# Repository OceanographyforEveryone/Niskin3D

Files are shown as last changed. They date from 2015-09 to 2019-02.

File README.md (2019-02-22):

Niskin3D
========

### Background

Niskin3D is low-cost, open-source water sampler made from 3D-printed parts and controlled by a waterproof servo. 

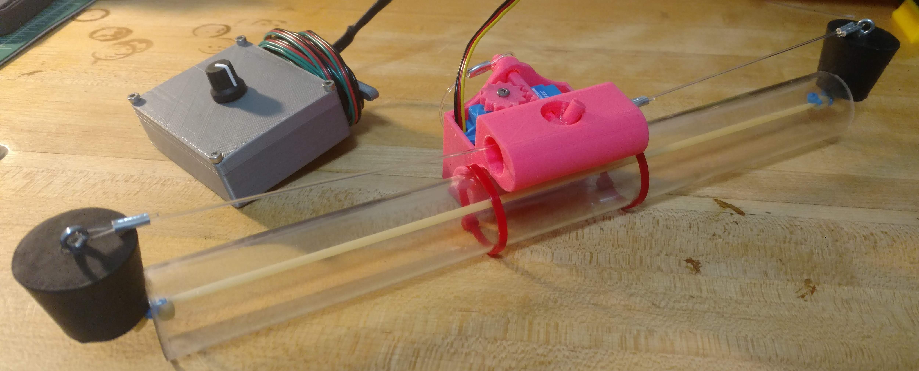
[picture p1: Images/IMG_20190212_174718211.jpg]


### Overview

The Niskin bottle, a seemingly simple tube designed to take water samples at discrete depths, is one of the most important tools of oceanography. Coupled with a CTD, an array of Niskin bottles fit into a rosette provides everything an oceanographer needs to profile the ocean. Niskin bottles are neither cheap nor particularly easy to use. A commercial rosette requires a winch to launch and recover, requiring both a vessel and a crew to deploy. For informal, unaffiliated, or unfunded researchers, as well as citizen scientists or any researcher working on a tight budget, getting high-quality, discrete water samples is an ongoing challenge. 

The Niskin3D lowers the cost of discrete-depth water sampling and makes this common tool of oceanographic research available to anyone. 

### Current Status

Undergoing major redesign as of 2/12/2019.

### Bill of Materials

We use Amazon Affiliate links because the small kickback helps fund more projects like this, but almost everything can be sourced through hobby shops, hardware stores, and other retailers. These recommendations don't necessarily represent the cheapest prices but rather the actual components we bought for this project or the closest approximation we could find. Some components are batched and may be available elsewhere in smaller quantities. Other high-test line and elastics can be used in place of the monofilament and sligshot tubing. 

**Niskin3D Bottle and Trigger Mechanism**

Part | Supplier | Price | Link
--- | --- | --- | ---
HiTec 32646W HS-646WP Water Proof Analog Servo (IP-67 Rated) | Amazon | $44.36 | https://amzn.to/2E60NLb
Clear Polycarbonate Tubing, 1-1/8" ID, 1-1/4" OD, 1/16" Wall, 4' Length | Amazon | $11.72| https://amzn.to/2E66wRa
Solid Rubber Stoppers - Size 6 | Amazon or local hardware store | $10.88 | https://amzn.to/2E6pEyw
Eye Screw with 12mm hoop | Amazon or local hardware store | $6.89 | https://amzn.to/2U5frI4
150-lb Monofilament with 1.3mm Crimps | Amazon or local fishing store | $12.99 | https://amzn.to/2tmStAh
3x5mm Natural Latex Rubber Band Tube Tubing for Slingshots | Amazon or local sportiing good store | $7.55 | https://amzn.to/2GGn57R
8" Cable Ties | Amazon or local hardware store | $6.99 | https://amzn.to/2E7rf76

**Niskin3D Control Box**

Part | Supplier | Price | Link
--- | --- | --- | ---
Arduino Leonardo | Amazon or Arduino.org | $22.19 | https://amzn.to/2E66RDo
2K Ohm Potentiometer | Amazon | $13.21 | https://amzn.to/2SGJUil
Ribbon Cable | Amazon | $6.98 | https://amzn.to/2UPQDDK
M3 Hex Socket Screws | Amazon | $10.99 | https://amzn.to/2GnfeN8

Consumables include heat shrink tubing, solder, and hook-up wire. Tools include a crimper, flush cut pliers, hex wrench, and a soldering station. We recommend using PLA filament for the 3D-printable parts. 

### Build Instructions

**3D Printing.** Print all parts in [3D_Printer_Files](https://github.com/OceanographyforEveryone/Niskin3D/tree/master/3D_Printer_Files) (ignore the folder labelled old unless you want to build the original Niskin3D) using your prefered PLA filament. NiskinRecieverLinear.stl, PowerBox.stl, and PowerBoxBottom.stl should be printed at 200 micron resolution with 20% infill. All other components should be printed at 100 micro resolution with 100% infill. 

**Servo Assembly.** Remove the included servo horn and slot the servo wheel onto the exposed metal gear. Use the included screw to secure the wheel. 

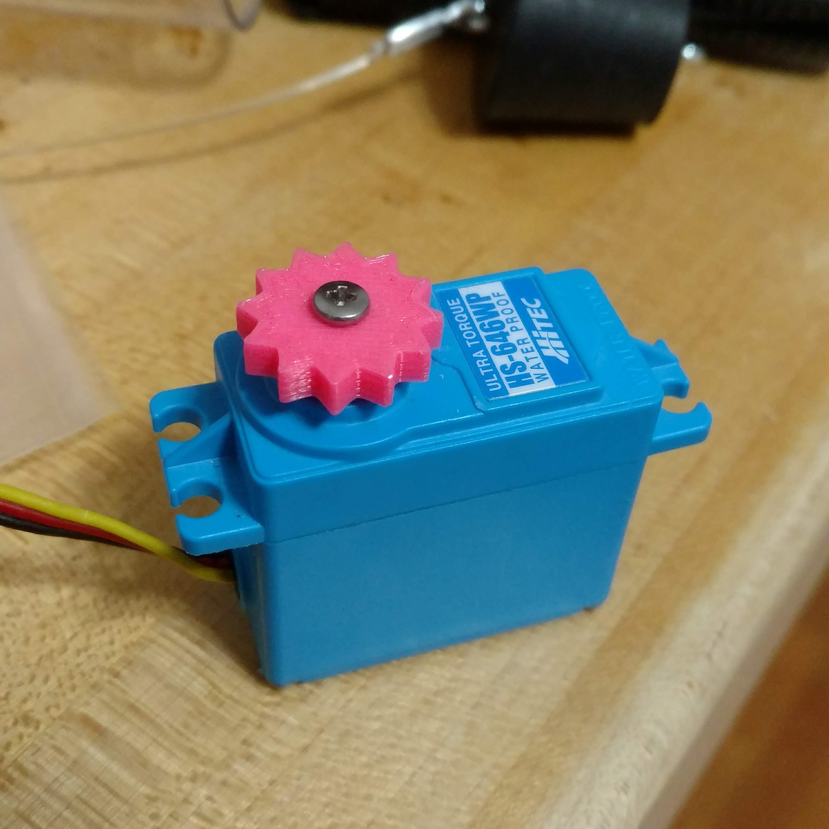
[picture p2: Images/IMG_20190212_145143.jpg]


**Receiver Assembly.** Insert the servo into the reciever such that when holding the reciever with the trigger tube facing away from you, the servo wheel sits to the right of the trigger slot. 

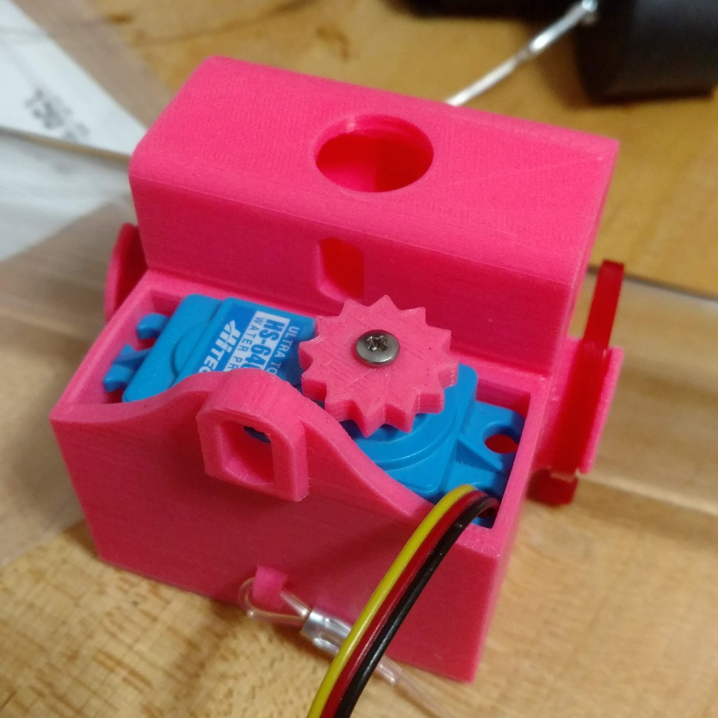
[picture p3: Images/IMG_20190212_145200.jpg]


Rotate the servo wheel counter-clockwise until it reaches its limit. Slot the trigger through the external trigger hole and across the servo wheel and just barely into the main trigger slot. The innermost tooth of the trigger should fully catch against the servo wheel. Secure the trigger to the reciever by looping monofilament through the hole in the trigger and the loop near the base of the reciever to prevent the trigger from being lost if it comes loose.

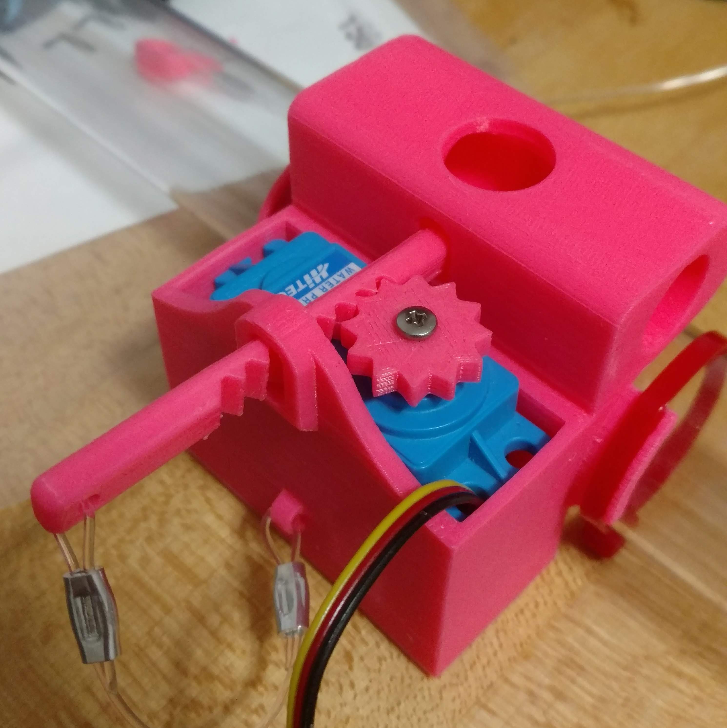
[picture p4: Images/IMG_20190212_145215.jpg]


**Bottle Assembly.** Cut the polcarbonate tube to the deisred length. Screw the eye screws into the center of both faces of the rubber stopper. Crimp monofilament onto the wider face of each stopper. On one stopper, measure out enough line to reach the hole in the center of the reciever trigger tube and crimp a large loop into the monofilament. On the other stopper, measure out enough line to  reach the hole in the center of the reciever trigger tube with enough length the the pin can sit in the center of the trigger tube and crimp the monofilament around the pin with enough slack that the line can sit in the notch on the pin. 

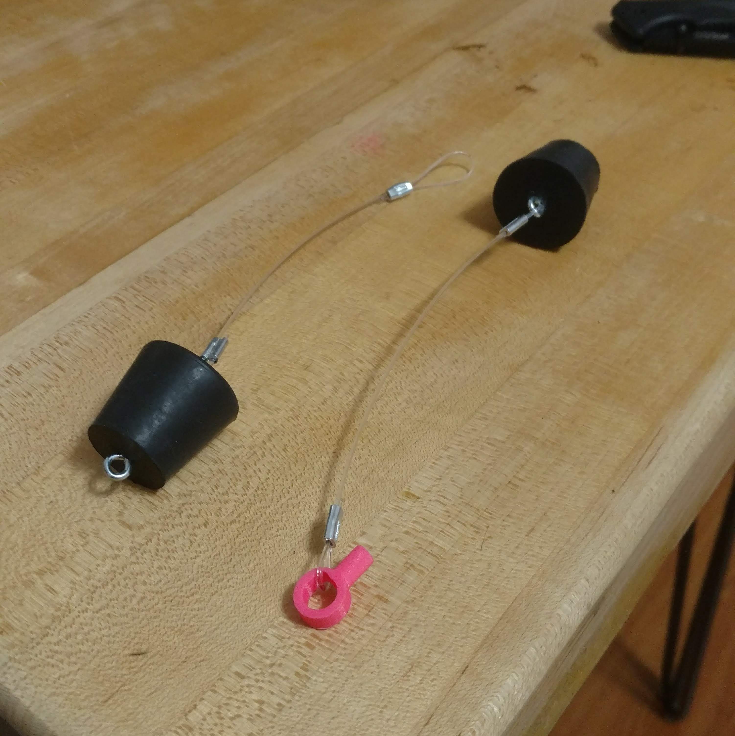
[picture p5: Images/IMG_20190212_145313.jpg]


Measure out enough latex tubing that it can hold the two rubber stoppers tightly in the polycarbonate tube. On the inner face of one rubber stopper, ziptie the latex tubing to the eye bolt. Feed the latex tubing through the polycarbonate tube, pull it tight, and ziptie it to the inner eye bolt on the other rubber stopper. 

**Power Box Assembly.** _Only do this if you need an independently-triggered Niskin bottle. Otherwise, connect the servo to the hardware of your choice using a standard servo interface._  Flash [NiskinServo.ino](https://github.com/OceanographyforEveryone/Niskin3D/tree/master/NiskinServo) to the Arduino. Solder header wires to the potentiometer. Screw the potentiometer into the large hole in the center of the Power Box Bottom. Connect the outer leads of the potentiometer to ground and Vin. Connect the center lead to Analog Pin 0. Measure out as much ribbon cable as you need for the servo. Feed ribbon cable through hole next to the spool on the case. Connect servo to ground and 5V. Connect signal line to Digital Pin 7. Close case and secure with M3 screws.

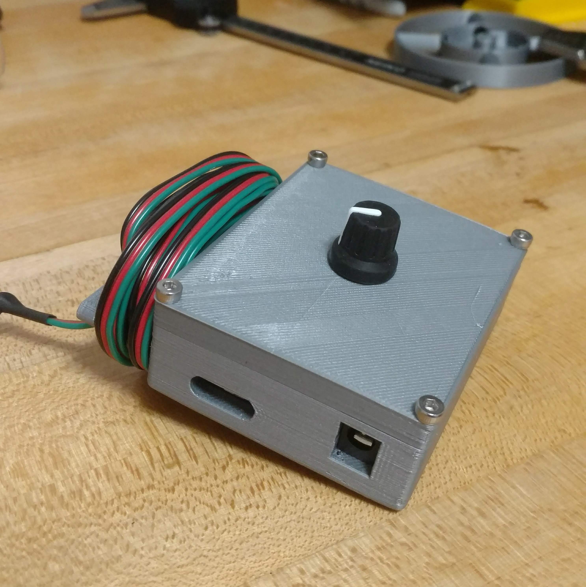
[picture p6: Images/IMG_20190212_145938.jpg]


### Priming the trigger

Pull the rubber stoppers out of the polycarbonate tube. Slot the pin into the trigger tube such that the point sticks up through the central hole. Rotate the servo clockwise to drive the trigger through the pin and into the wall of the trigger tube. Slot the loop on the other stopper through the trigger tube and over the pin such that it catches and rotates the pin towards the opposite rubber stopper. 

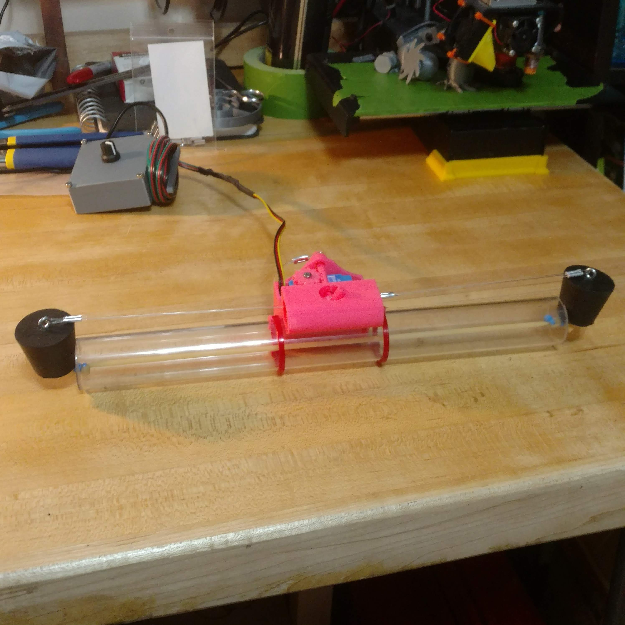
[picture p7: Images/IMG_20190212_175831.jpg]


Ensure that the rubber stoppers are situated so that once the pin is released both stoppers will be pulled into the polycarbonate tube and seal it. 

Your Niskin bottle is now primed. 

### Triggering

Activate the servo and rotate it counter-clockwise to pull the trigger and release the pin. 

### Resources and Media

[Oceanography for Everyone](http://oceanographyforeveryone.com/)

[Niskin3D: the open-source water sampler](https://www.thingiverse.com/thing:3421202)

[A 3D-printable, drone and ROV-mountable, water sampler](http://www.southernfriedscience.com/?p=18730)

[The next generation open-source, 3D-printable Niskin bottle has arrived!](http://www.southernfriedscience.com/the-next-generation-open-source-3d-printable-niskin-bottle-has-arrived/)

### Acknowledgments 

Design and testing of the Niskin3D conducted by Andrew Thaler.

### Code of Conduct

Please review our [Contributor Code of Conduct](https://github.com/OceanographyforEveryone/Niskin3D/blob/master/CODE_OF_CONDUCT.md) prior to your first contribution.

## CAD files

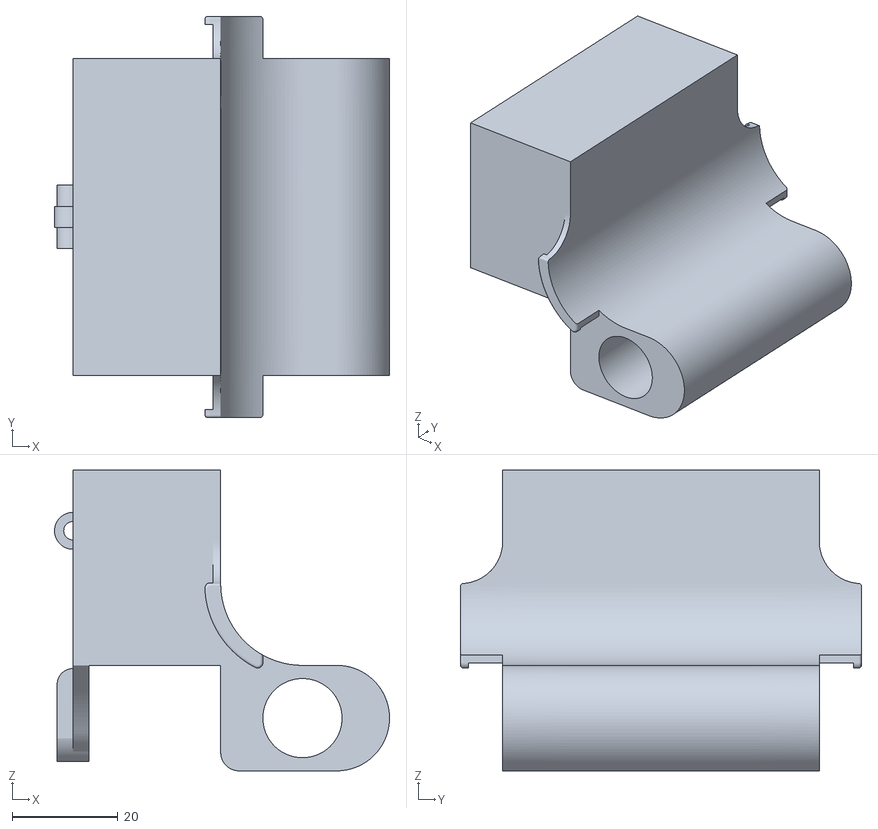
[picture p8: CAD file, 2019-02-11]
3D_Printer_Files/NiskinRecieverLinear.stl
63.5 x 76.0 x 57.0

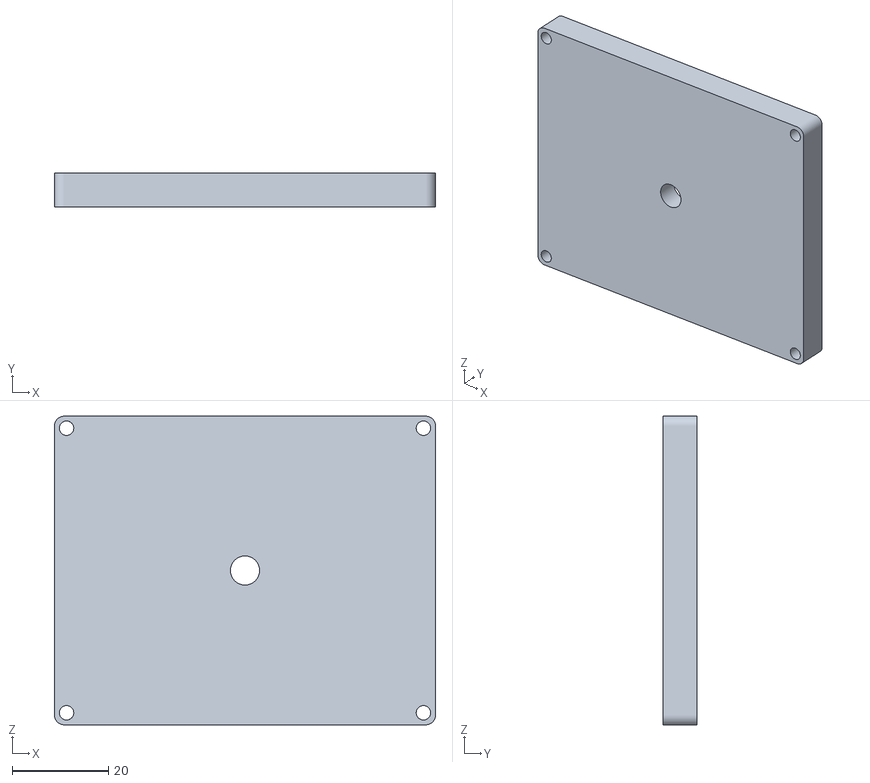
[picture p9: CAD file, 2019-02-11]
3D_Printer_Files/PowerBoxBottom.stl
79.0 x 7.00 x 64.0

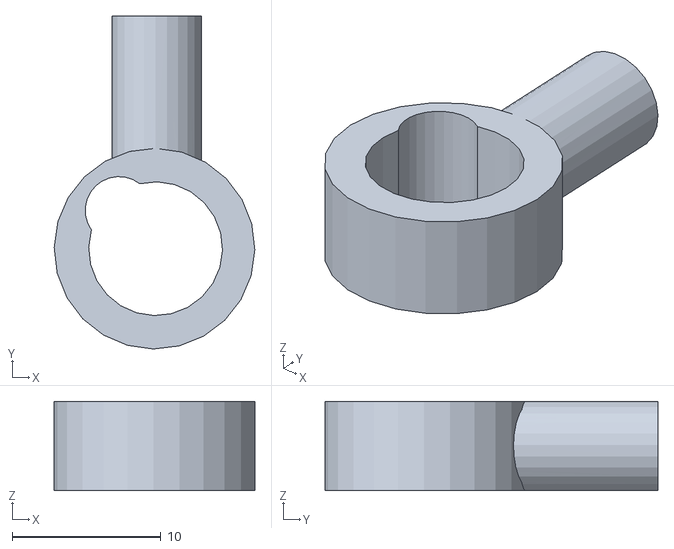
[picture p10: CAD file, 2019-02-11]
3D_Printer_Files/Niskin3DPin.stl
13.5 x 22.4 x 6.00

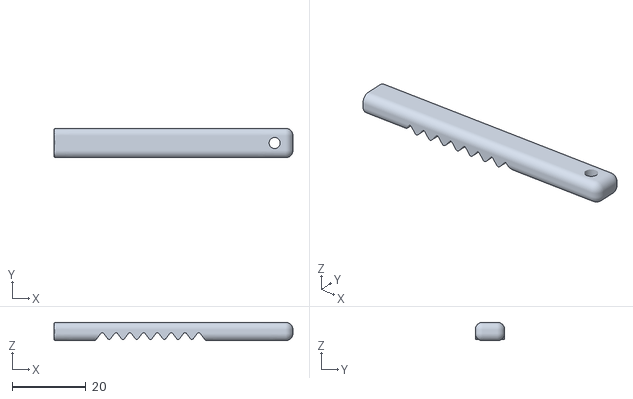
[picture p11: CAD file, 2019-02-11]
3D_Printer_Files/NiskinTriggerLinear.stl
65.0 x 8.00 x 5.00

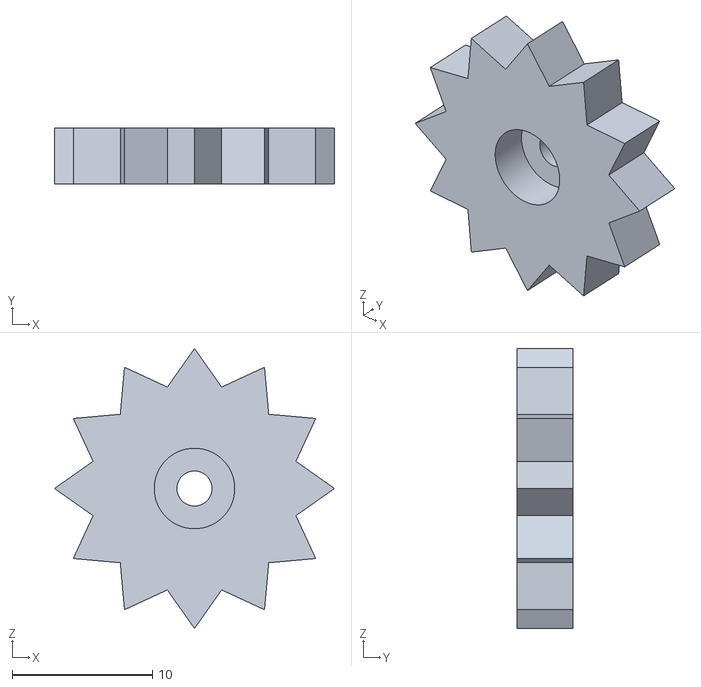
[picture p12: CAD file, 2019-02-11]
3D_Printer_Files/ServoWheel.stl
20.0 x 4.00 x 20.0

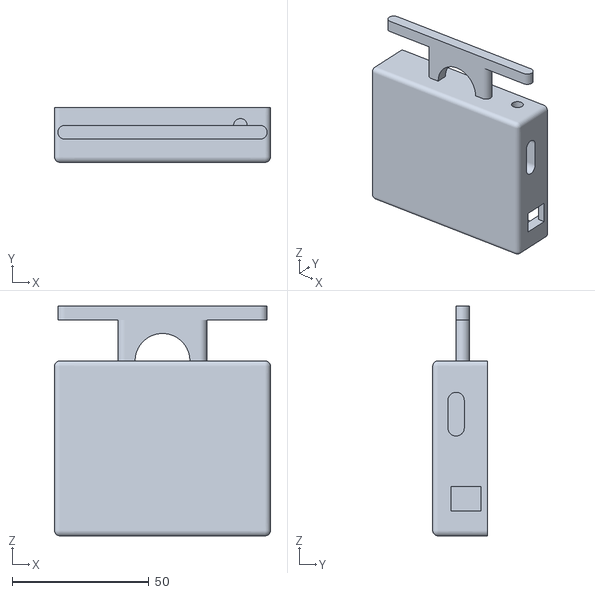
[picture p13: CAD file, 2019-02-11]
3D_Printer_Files/PowerBox.stl
79.0 x 20.0 x 84.0

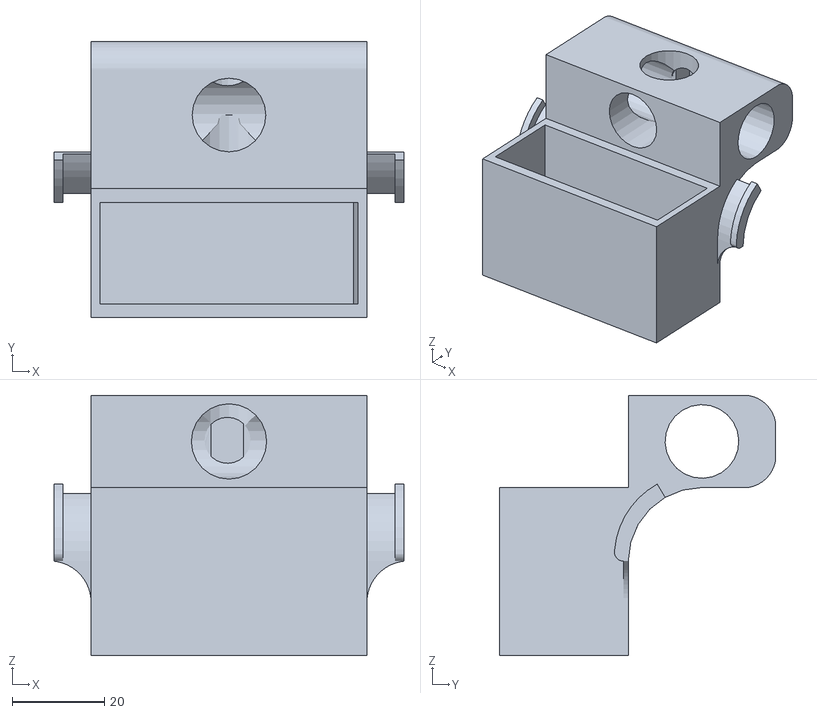
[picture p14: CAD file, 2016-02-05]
3D_Printer_Files/NiskinRecieverHS646WP.stl
76.0 x 60.0 x 56.5

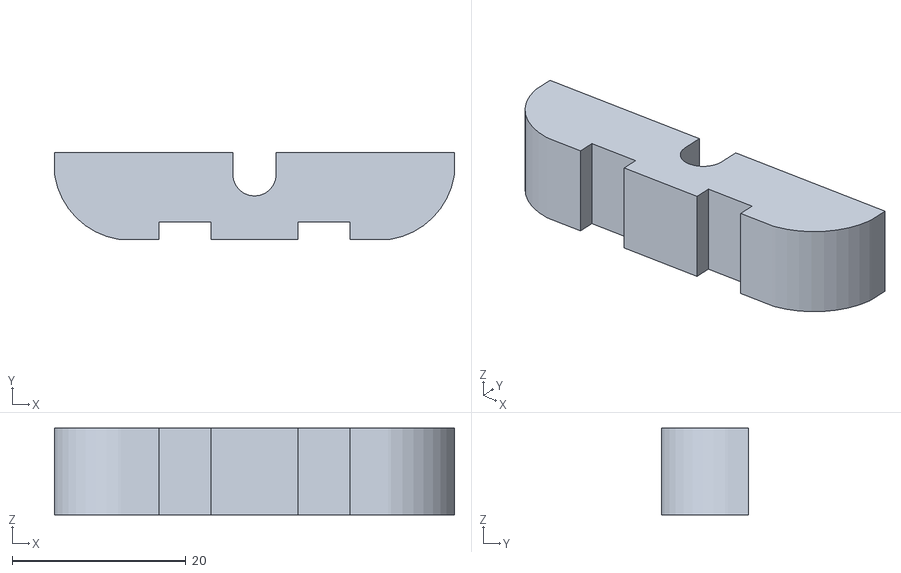
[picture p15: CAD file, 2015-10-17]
3D_Printer_Files/OpenROVNiskinRear.stl
46.0 x 10.0 x 10.00

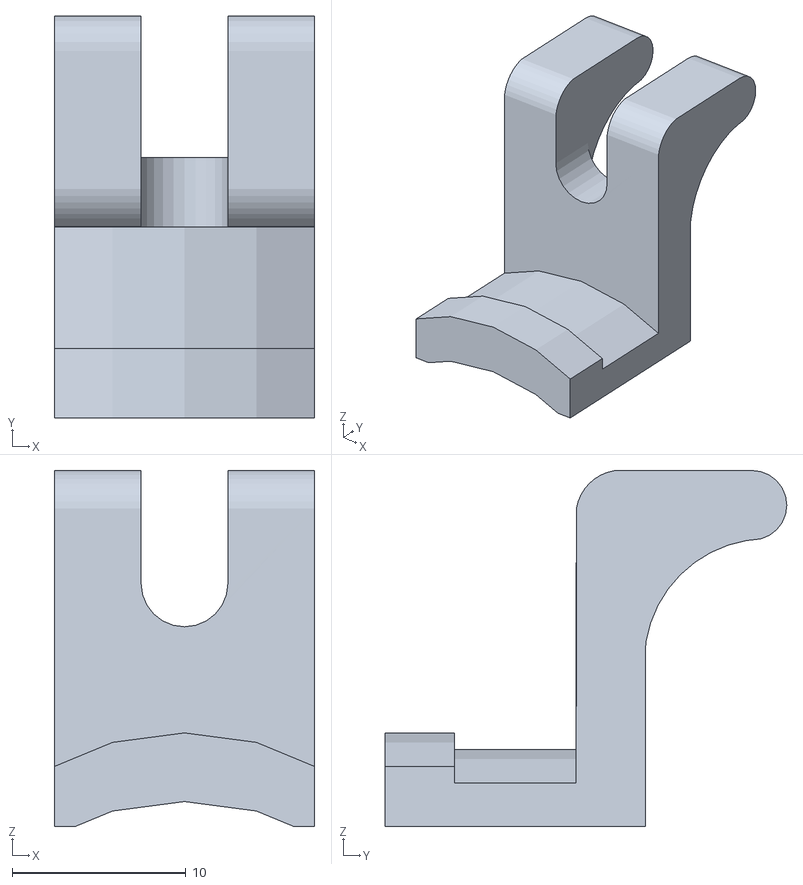
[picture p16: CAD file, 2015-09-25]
3D_Printer_Files/NiskinEndCatch.stl
15.0 x 23.1 x 20.5

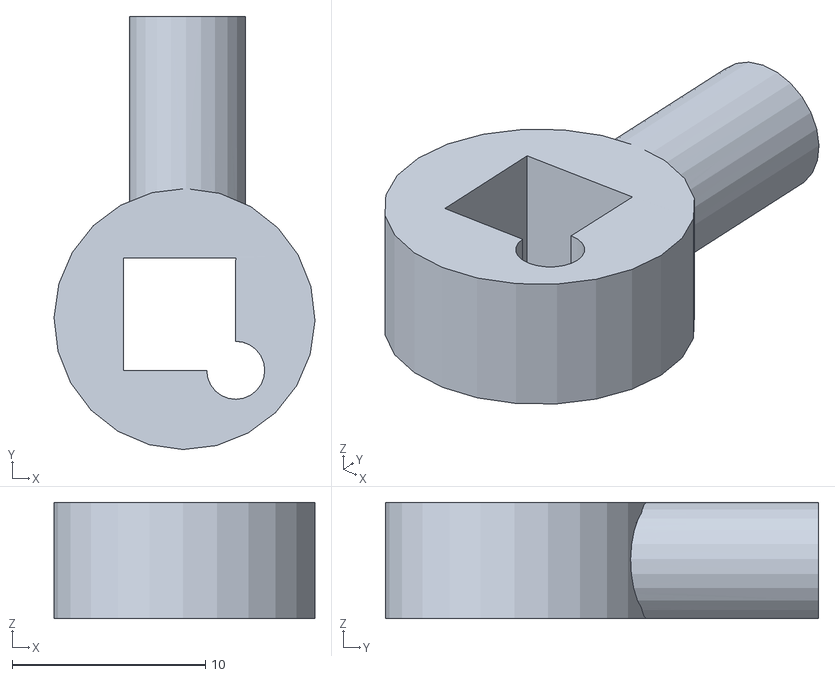
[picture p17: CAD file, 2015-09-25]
3D_Printer_Files/NiskinPin.stl
13.5 x 22.4 x 6.00

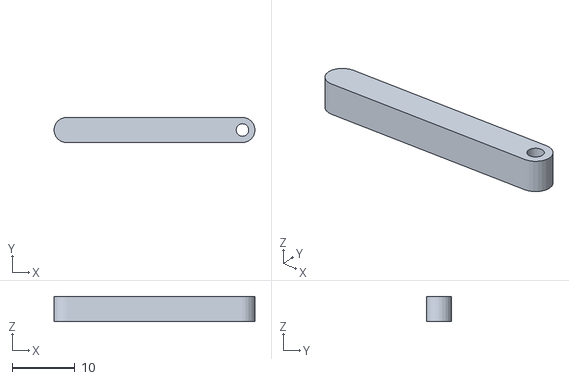
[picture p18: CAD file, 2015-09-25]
3D_Printer_Files/NiskinTrigger.stl
32.0 x 4.00 x 4.00

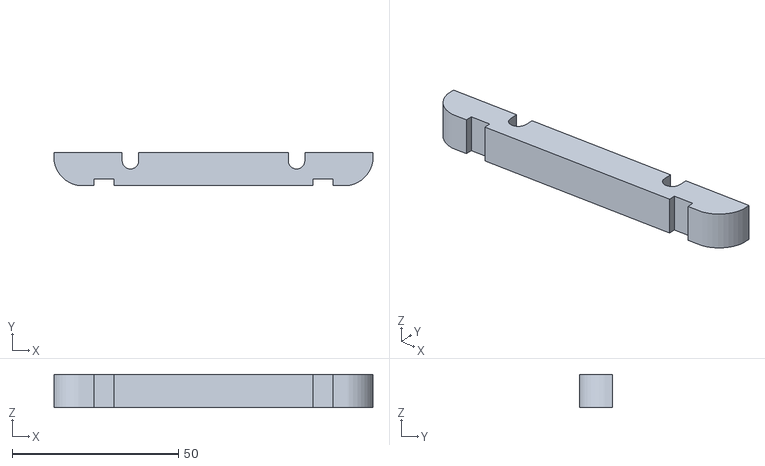
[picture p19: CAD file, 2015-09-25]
3D_Printer_Files/OpenROVNiskinFront.stl
96.0 x 10.0 x 10.00

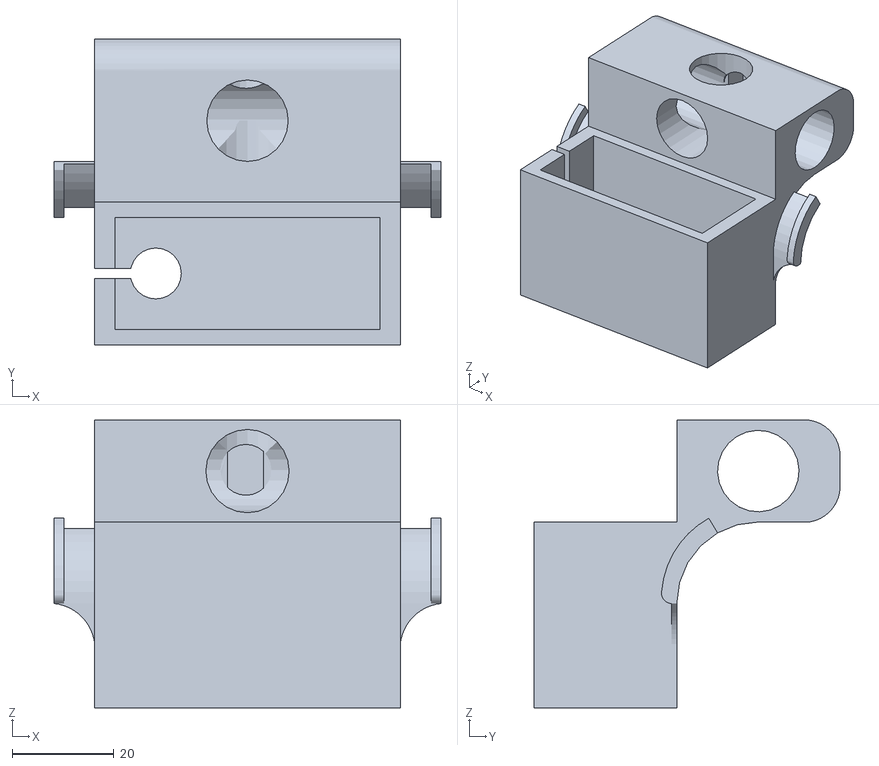
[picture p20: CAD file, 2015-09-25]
3D_Printer_Files/NiskinReciever.stl
76.0 x 60.0 x 56.5

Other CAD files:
3D_Printer_Files/NiskinEndCatch.skp
3D_Printer_Files/NiskinPin.skp
3D_Printer_Files/NiskinReciever.skp
3D_Printer_Files/NiskinRecieverHS646WP.skp
3D_Printer_Files/NiskinTrigger.skp
3D_Printer_Files/Old/NiskinEndCatch.skp
3D_Printer_Files/Old/NiskinPin.skp
3D_Printer_Files/Old/NiskinReciever.skp
3D_Printer_Files/Old/NiskinRecieverHS646WP.skp
3D_Printer_Files/Old/NiskinTrigger.skp
3D_Printer_Files/Old/OpenROVNiskinFront.skp
3D_Printer_Files/Old/OpenROVNiskinRear.skp
3D_Printer_Files/OpenROVNiskinFront.skp
3D_Printer_Files/OpenROVNiskinRear.skp

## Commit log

2015-09-25 Add 3D Printer Files
    5 Files for the Niskin3D
    [NiskinEndCatch.stl, NiskinOpenROVClip.stl, NiskinPin.stl, NiskinReciever.stl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]
2015-10-13 Added Current Status
2015-10-17 Added Sketchup Files
    [NiskinEndCatch.skp, NiskinPin.skp, NiskinReciever.skp, NiskinTrigger.skp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]
2016-01-11 New Receiver for HS646WP waterproof servo
    Adapted the receiver for a different waterproof servo, which will
    require some modification to work in deeper water.
    [NiskinRecieverHS646WP.skp, NiskinRecieverHS646WP.stl]
2016-02-05 Resized for new servo, final fit test
    Very snug, but a solid fit.
    [NiskinRecieverHS646WP.skp, NiskinRecieverHS646WP.stl]
2016-05-20 Updated Files
    [NiskinRecieverHS646WP.skp]
2019-02-11 Uploaded New Niskin Design
    [NiskinEndCatch.skp, NiskinEndCatch.stl, NiskinPin.skp, NiskinPin.stl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]
